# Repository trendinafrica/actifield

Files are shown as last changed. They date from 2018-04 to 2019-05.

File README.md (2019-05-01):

# README  

## Welcome! Or as we say it in Ghana, *Akwaaba!*

This is the Actifield project repository and we’re excited to have you here. 

This document (the README file) is a hub to help you find your way around. Feel free to jump straight to one of the sections below or just scroll down to find our more.

## What are we doing? (and why?)

### The problem

Prohibitive costs is one of the key factors that limit access to science equipment particularly in lesser funded institutions and countries.
This affects the quality of science education and research in these institutions.
As a graduate student I grew frustrated with this problem when I had to modify or abandon some experiments because I did not have the needed equipment.  So I decided to build my own equipment.
I and my friends started this project because we realised we could build some of the equipment we needed on our own by taking advantage of open source designs and code. 
 
### The solution

The [Open Science hardware](http://openhardware.science/) movement has gained popularity in recent years. Using open source designs, code and tools, scientists can now build and customise their own equipment, usually at a fraction of the cost of commercial versions. However, this movement is relatively new to African scientists who may not have the skills to build their own equipment. 

Therefore this project was initiated to build and document some equipment as a step in tackling this problem. We chose to build an actimeter as our first equipment because it is routinely used in experiments in our faculty and the current approach is a very laborious task of manually tracking experiment videos.

## Who we are??
This project was initiated by me, [Victor](https://twitter.com/v_kumbol), and my friends, [Eli](https://twitter.com/AmpofoElikplim) and [Mary](https://twitter.com/mary_twumasi) while we were graduate students at the [Kwame Nkrumah University of Technology](https://www.knust.edu.gh/) in Ghana. 

The project was supported by the generous mentorship and funding we received during the [1st TReND Advanced Open Labware Workshop](http://trendinafrica.org) in April 2018. 

I also received further support and mentorship to reorganise this repository while participating in the 14th Cohort of the Mozilla Open Leaders program.

## What is an actimeter? 
We’re building an equipment called an actimeter. At the simplest, the actimeter is used to measure and record the locomotor activity - how fast or slow a test animal (usually rodents), is moving. This information is useful for several tests such as screening for potentially toxic effects of a new drug on the brain. 

However, beyond these basic tests. An actimeter can be modified to provide more information for example, detecting behaviours in rodents that indicate anxiety or fear. We developed this project for scientists who need a simple and inexpensive actimeter that can be easily built. 

By providing scientists with the resources (designs and code) to build their own actimeter, this project will help scientists in several ways: 
1. Reduce spending for the purchase, repair and maintenance of proprietary equipment
2. Save time by automating laborious tasks e.g. manual video tracking methods
3. Improve teaching since the equipment can be used for practical demonstrations in undergraduate labs 
4. Allow scientists to customise the device for other experiments
5. Increase reproducibility of experiments since the equipment is fully documented

## What do we need
Everyone! In whatever way you can help.

We need expertise in the following areas 
*Neuroscience
*User interface (UI)/ User experience (UX) design
*Computer Aided Design (CAD)
*Electronics
*Arduino
*Technical writing
*Web Development
*Mentorship

## Get involved
If you can help in any of the areas listed above or in any of the many areas that we haven't yet thought of, then please check out our [roadmap](ROADMAP.md) and [contribution guidelines](CONTRIBUTING.md).

Please note that it's very important to us that we maintain a positive and supportive environment for everyone who wants to participate. When you join us we ask that you follow our [code of conduct](CODE_OF_CONDUCT.md) in all interactions both on and offline.

## How can you use it?
If you want to customise Actifield, feel free to download or fork the repository and adapt the content (designs and code) to suit your needs. Everything here is freely reusable.

If you need help with building your own actimeter don’t hesitate to get in touch.

## Contact Us
If you have any questions or suggestions, you can simply open an issue here in this repository. You can also send Victor an <A HREF="mailto:kumbolvictor@gmail.com">email</A>. Wanna hang out on social media? Follow me on [Twitter](https://twitter.com/v_kumbol).

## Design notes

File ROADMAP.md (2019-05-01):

# Roadmap

Hello there!😃 You’re welcome to the Roadmap of the Actifield project. 

This document identifies the project's vision, its current status, and how to reach the project’s end goal. It helps contributors keep track of the overall status of the project and recognize where their help is most needed. Please note that the roadmap is subject to change, and that contributions are also welcome to the document.

## Project Vision
We are working with scientists and developers in Ghana to build a local open hardware community to empower scientists to develop their own lab equipment. We are currently working on upgrading, Actifield, a device for behavioural experiments that we developed for neuroscientists.

## Project Summary
We’re building an equipment called an actimeter. At the simplest, the actimeter is used to measure and record the locomotor activity - how fast or slow a test animal (usually rodents), is moving. More details about Actifield [here](Project_Description.md). 

We developed this project for scientists who need a simple and inexpensive equipment that can be easily built. 
 
## Milestones

Down below are a list of milestones that represent the overall goals of the project. Preferably, they are to be done in sequential order. But you can help in any task you feel comfortable with. Please read our [Contribution Guidelines](CONTRIBUTING.md) and our [Code of Conduct](CODE_OF_CONDUCT.md) 😉

### Short term: During Sprint for Internet Health (May 2019)

- [ ] **Get first community contribution**
> A community member files an issue or adds a pull request.

- [ ] **Display live graphs of activity counts on screen**
> Figure out how to display the results as a live graph on the computer screen. Check out this [issue](https://github.com/trendinafrica/actifield/issues/2)

- [ ] **Display an onscreen grid showing the current location of the mouse in the activity cage**
> Figure out how to determine and show the realtime location of the mouse in the test arena. Check out this [issue](https://github.com/trendinafrica/actifield/issues/3)

- [ ] **Build graphical interface to control the device from the computer**
> More on this [here](https://github.com/trendinafrica/actifield/issues/5)

- [ ] **Check available disk space on SD card before recording counts**
> More on this [here](https://github.com/trendinafrica/actifield/issues/4).

### Medium term: June - August, 2019 

- [ ] **Create manual for users to build or customise the device**
> Write a manual to guide new users to build or customise the device. Check out this [issue](https://github.com/trendinafrica/actifield/issues/6)

- [ ] **Build project website**
> Build website (a [GitHub page](https://pages.github.com/)) to make it easier for users to find and explore our material. with useful resources for African scientists interested in developing their own equipment

- [ ] **Organise training workshop**
> Organise training workshop on building open labware for Ghanaian scientists 

### Completed
- [x] **Build first prototype of Actifield**
> The first prototype of Actified has been built and the designs uploaded onto GitHub.

- [x] **Publish Actifield in a journal**
> Actifield was published in [HardwareX](https://www.sciencedirect.com/science/article/pii/S2468067218300695). This will help provide credibility for academic users and a reference to be cited when used in research works.

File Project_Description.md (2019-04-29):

# Project Description

## Introduction 
The activity meter box is used in neurobehavioral tests to examine the effects of various treatments on the activity level of mice and rats. Our proposed project dubbed “ActiField” is an Arduino-powered activity meter box which can be used to measure locomotor activity of rodents. Locomotor activity is used to evaluate the central effects of drugs. Locomotor activity testing can also reveal possible confounding effects in other tests that rely on motion such as the passive avoidance test for memory. As an additional feature, the ActiField system can be used to automate the open field test, another widely used test for anxiolytic or anxiogenic behaviour. 

## Components
Below is a description of the main components of the ActiField system.

Testing Chamber: The testing chamber is a cuboid plastic box (22×22×30 cm) with a removable transparent cover.

IR Grid: Four panels of 11 IR break beam sensors spaced 2 cm apart are fixed to the inner walls of the testing chamber close to the floor. Each break beam sensor is supplied as a pair of diodes; one diode emits IR beam while the other detects the IR beam. Two panels hold the emitting IR diodes and the other two hold the receiving IR diodes. Receiving and emitting sets will be fixed on opposite sides of the testing chamber to generate a grid of IR beams of 2×2 cm mesh size. As the rodent moves in the testing chamber, the IR beams will be broken and this activity will be transmitted to the microcontroller for processing.

Processing Unit: An Arduino Mega 2560 microcontroller serves as the processor of the system. Inputs from the infrared sensors are fed to the Arduino and processed. The output is displayed online on an attached LCD Screen. Also, a data logging shield is mounted the Arduino for storage of experimental data on an SD. The Arduino can be powered from the mains with a 9 V DC adaptor, a 9 V battery or by a computer.

Display Unit: This consists of a 16×2 LCD screen connected to the Arduino by an i2C LCD backpack. The LCD shows the activity count (total number of beam breaks) and the location of the rodent (centre/periphery) from the system in real time.

## Operation
In our proposed project, ActiField, an Arduino Mega 2560 microcontroller serves as the core processor of the system. Once the code is uploaded to the microcontroller, ActiField can run independently with power from a 9V alkaline battery without the need for a computer or monitor. This is a particularly advantage in settings with erratic or unstable power supply. The system functions automatically and independently according to the code uploaded to the microcontroller. 

Once the system is powered and the code is uploaded, the ActiField system is ready for testing. The mouse or rat to be tested is placed into the test chamber and as the rodent moves in the test chamber it breaks the IR beams in the “grid”. The break beam sensors detect and transmit these signals via the connecting cables to the Arduino. The Arduino keeps a tally of the number of beam breaks and displays the current total on the LCD screen which is mounted on a display unit separate from the test chamber. In most studies, activity counts are expressed at fixed time intervals over the entire test duration. This feature is built into the ActiField system. At a user set frequency (default every 5 min), the Arduino writes the activity count to a file on an SD card mounted on the data logging shield. The user can retrieve this data after the experiment for subsequent analysis on a computer. 
This is the basic functionality of the system however we envisage at least two additional features described below.
Firstly, the ActiField system can be set up to determine the location of the rodent in the test chamber. The IR beams in the test chamber are set up in a grid which represents a coordinate system. Hence, the location of the rodent in the test chamber can be determined based on the set of beams which are broken at a given time. This will require further refinement of the code.
Secondly, the ActiField system can be set up for real time display and graphing of activity counts. This can be made possible by connecting the Arduino to a computer using a USB cable for online display and graphing of the data. We have plans to develop the software to enable this feature using the Processing programming language after building the project. 

## Validation
We intend to validate the system by live video analysis of mice in the test chamber with a video analysis software e.g. Any MAZE or EthoVision concurrently with the ActiField system and comparing the results obtained for correlation.

## Conclusion
In this work, we describe the components and operation of the ActiField system, our proposed real time, automated activity meter box. In this system, low cost components e.g. microcontroller, IR sensors, LCD screen are used to achieve the objectives of the proposed design.

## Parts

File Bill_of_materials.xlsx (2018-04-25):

Part Name | Detail1 | Detail2 | Detail3 | Quantity | Cost per unit | Total cost | Link to supplier/part
Arduino Mega 2560 |  |  |  | 1 | £ 21.99 | £ 21.99 | https://www.conrad.de/de/joy-it-kompatibles-board-arduino-mega-2560r3-1409778.html
Breadboard |  |  |  | 1 | £3.75 | £3.75 | https://www.pollin.de/p/labor-steckboard-510174
Breadboard (empty PCB for soldering) |  |  |  | 20 | £4.09 |  | https://www.conrad.de/de/platine-hartpapier-l-x-b-160-mm-x-100-mm-35-m-rastermass-254-mm-wr-rademacher-wr-typ-790-5-inhalt-1-st-529618.html?sc.ref=Search%20Re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
 |  |  |  | 10 |  | £0.00 | https://www.pollin.de/p/9v-blockbatterien-duracell-industrial-10-stueck-271253
Battery Contact | 9 V |  |  | 10 | £ 0.49 | £ 4.90 | https://www.conrad.de/de/batterieclip-1x-9-v-block-druckknopfanschluss-l-x-b-31-mm-x-14-mm-tru-components-bs-er-36-150-1663957.html
Wire to Board Standard Terminal Block | 12 Contacts |  |  | 3 | £5.48 | £16.44 | http://uk.farnell.com/camdenboss/ctb0708-12/tb-wire-to-brd-12pos-12awg/dp/2315272
Lithium Battery CR1220 | 3 V | 38 mAh | 12.5 mm | 1 | £ 1.19 | £ - | http://uk.farnell.com/multicomp/cr1220/coin-cell-lithium-3v-38mah-cr1220/dp/2065165
soldering iron |  |  |  | 9 | £5.25 | £47.25 | https://www.pollin.de/p/loetkolben-daytools-lk-45w-840195
Solder Wire | 0.7mm |  |  | 1 | £0.82 | £0.82 | http://uk.farnell.com/multicore-solder/d9922-2metre/solder-wire-99-3-0-7-227deg-0/dp/9887105
soldering grease |  |  |  | 9 | £1.15 | £10.35 | https://www.pollin.de/p/loetfett-30-g-840206
Screw driver set | 8 pieces with electic tester |  |  | £1.00 | £7.95 | 71.55 | https://www.pollin.de/p/vde-schraubendreher-set-8-teilig-501143
screw driver set small bits | 36 pieces |  |  | £1.00 | 4.95 | £39.60 | https://www.pollin.de/p/feinmechanik-bitsatz-mit-schraubendrehergriff-36-teilig-501018
Power Distribution Bus |  | 7 x 6mm |  | 8 | $1.95 | $15.60 | https://www.adafruit.com/product/737
IR Break Beam Sensor | 3mm LED |  |  | 25 | $1.95 | $48.75 | https://www.adafruit.com/product/2167
Jumper wires |  | 65 units bundle |  | 4 | $3.50 | $14.00 | https://www.pollin.de/p/steckbruecken-sortiment-65-teilig-511007
crocodile cable (get a LOT) |  |  |  | 12 | $2.95 | $35.40 | https://www.pollin.de/p/messleitungen-mit-krokodilklemmen-0-5-mm2-200-mm-10-stueck-830593
Adafruit Assembled Data Logging shield for Arduino |  |  |  | 1 | $13.95 | $13.95 | https://www.adafruit.com/product/1141
i2c / SPI character LCD backpack |  |  |  | 1 | $9.95 | $9.95 | https://www.adafruit.com/product/292
Standard LCD 16x2 + extras | White on Blue |  |  | 1 | $9.95 | $9.95 | https://www.adafruit.com/product/181
multimeter |  |  |  | 5 | 19.95 | $99.75 | https://www.pollin.de/p/multimeter-mastech-ms8233e-ce15-830722
MikroSD karte | 16gb | class10 |  | 5 | 5.99 | 29.95
wire stripper |  |  |  | 9 | 3.25 | 29.25 | https://www.pollin.de/p/automatik-abisolierzange-500070
Packing tape | 6 units set |  |  | 2 | 4.99 | 9.98 | https://www.pollin.de/p/klebeband-kinzo-6er-set-891200
Electrical tape |  |  |  | 9 | 2.95 | 26.55 | https://www.pollin.de/p/elektriker-isolierband-19-mm-18-m-weiss-temperaturbestaendig-511240
LEDs |  |  |  | 2 | 1.95 | 3.9 | https://www.pollin.de/p/leuchtdioden-sortiment-100-teilig-800002
resistors | high power |  |  | 1 | 3.95 | 3.95 | https://www.pollin.de/p/sortiment-hochlast-widerstaende-1-17-w-100-stueck-800027
ribbon cable | 16wires | 28awg |  | 10 | 2.57 | 25.7 | https://www.conrad.de/de/flachbandkabel-rastermass-127-mm-16-x-008-mm-bunt-3m-7000058337-meterware-604069.html
allen key set | 10 pieces |  |  | 16 | 1.95 | 31.2 | https://www.pollin.de/p/innensechskant-schluesselsatz-10-teilig-501921
wire stripper |  |  |  | 9 | 3.25 | 29.25 | https://www.pollin.de/p/automatik-abisolierzange-500070
IR emitter | 5mm led |  |  | 25 | $0.81 | $20.25 | https://www.conrad.de/de/ir-emitter-940-nm-40-5-mm-rund-radial-bedrahtet-lite-on-lte-5208a-1127316.html
IR Detector | 5mm led | 940nm |  | 25 | $0.76 | $19.00 | https://www.conrad.de/de/ir-detektor-rund-radial-bedrahtet-5-mm-940-nm-20-lite-on-ltr-3208e-1127310.html

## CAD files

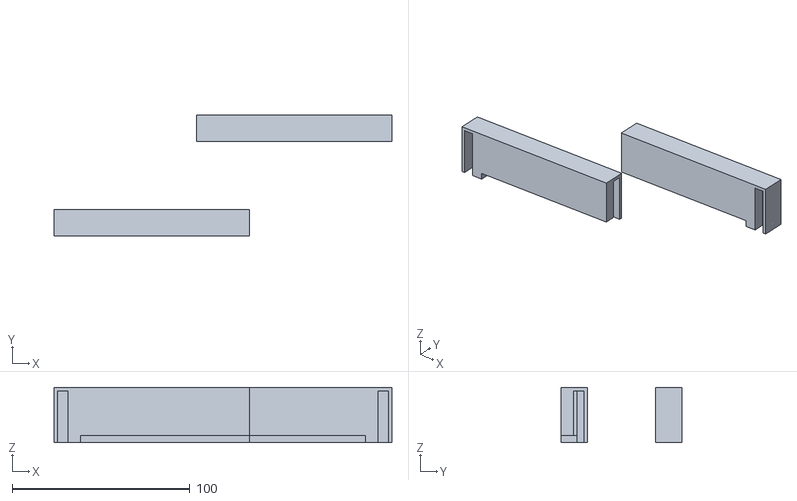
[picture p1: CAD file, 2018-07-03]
3D_print_designs/IR Panel B top.stl
190.0 x 68.0 x 31.0

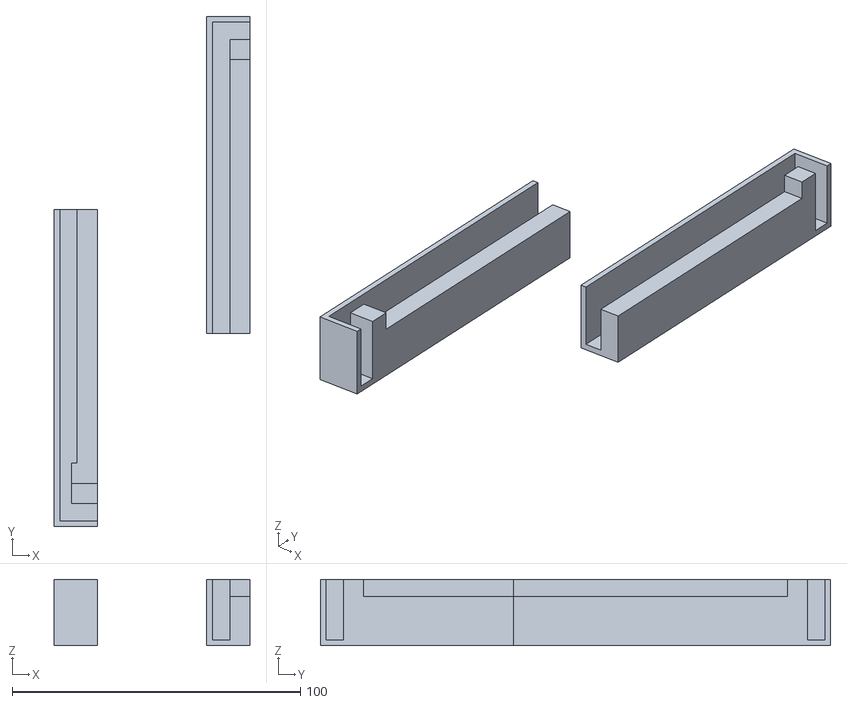
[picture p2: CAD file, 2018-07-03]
3D_print_designs/IR Panel B bottom.stl
68.0 x 177.0 x 23.0

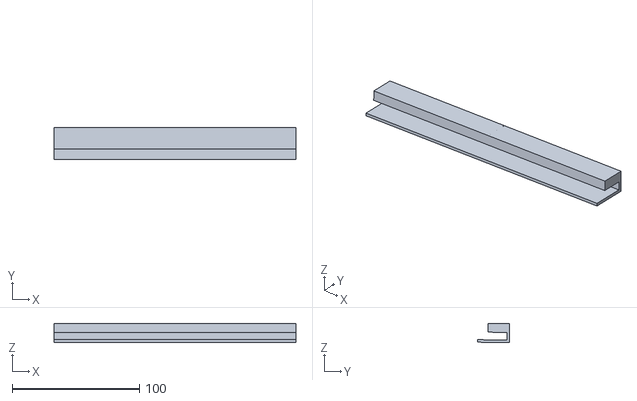
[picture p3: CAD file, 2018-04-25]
3D_print_designs/IR Panel A bottom.stl
190.0 x 25.3 x 15.3

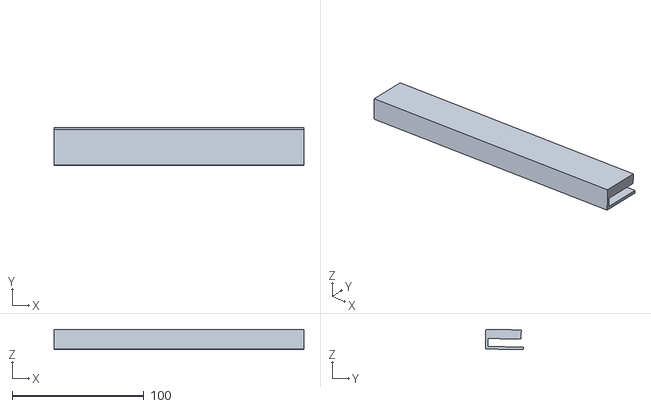
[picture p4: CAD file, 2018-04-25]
3D_print_designs/IR Panel A top.stl
190.0 x 29.0 x 15.5

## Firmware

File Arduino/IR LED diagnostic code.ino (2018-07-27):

int outPin = 13; // the pin number of the indicator LED
int outPinState = LOW; // the current state of the indicator LED
int count = 0; //this variable will store the number of beam breaks
int limit=50;                 //Threshold for detecting IR radiation 

// the following variables are long because the time, measured in miliseconds,
// will quickly become a bigger number than can be stored in an int.
long outTime = 0; // the last time the output pin was toggled

 //rows and cols will define the size of the array 
const int rows = 2;
const int cols = 8;
String pin;

int SensorMatrix[rows][cols] = {
  // This matrix will hold the pin assignments for the Sensors
  {0, 1, 2, 3, 4, 5, 6, 7}, 
  {8, 9, 10, 11, 12, 13, 14, 15}
};

int SensorStateMatrix[rows][cols] = {
 // This matrix will store the current reading from each sensor
  {0, 0, 0, 0, 0, 0, 0, 0},
  {0, 0, 0, 0, 0, 0, 0, 0}
};


void setup() {
Serial.begin(9600); //initialize serial monitor for writing
pinMode(outPin, OUTPUT); //set outPin as an output pin
} //close setup()

 
void loop() {
 
  //this nested for loop will scan each IR sensor in sequence
  for(int i = 0; i < rows; i++){
 
    for(int j = 0; j < cols; j++){
  SensorStateMatrix[i][j] = analogRead(SensorMatrix[i][j]); //read the current value of the corresponding sensor
  // if the beam was just broken (i.e. the sensor value went from > limit to <= limit) or restored (i.e. the sensor value went from <=limit to > limit),
    //int pin_no = SensorMatrix[i][j]+ 1
    pin = String(SensorMatrix[i][j] + 1);
    Serial.print("Pin "); 
    Serial.println(pin);  
    Serial.print(" reading = "); 
    Serial.println(SensorStateMatrix[i][j]);  
    delay(5); 
  }
 
    }//close for j
     Serial.println("");  
     Serial.println("");  
     Serial.println("");  
     delay(5000);
  }//close for i
 

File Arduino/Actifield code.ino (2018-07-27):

/*Created 7 July 2018
By Victor Kumbol
*/


#include <Wire.h>
#include <LiquidCrystal_I2C.h> //import libraries for LCD screen
#include <SD.h> //import the SD Card library
#include <SPI.h>

LiquidCrystal_I2C lcd(0x27,16,2);


int count = 0; //this variable will store the number of beam breaks
int threshold = 400; //Threshold for detecting IR radiation.This sets the sensitivity of the sensors
long runTime = 0; // this variable records the duration of the current test
long syncTime = 0; //this variable stores the last time the data was stored ot the SD card

File logfile; // the logging file


const long SYNC_INTERVAL = 60000; //mills between calls to flush()
const int chipSelect = 4; //the output pin for the SD card

String Sensor; //this stores the string type of the current sensor
String Count; //this variable stores the string type of the current beam-break count

int minutes;
int seconds;
int errors = false;

 //rows and cols will define the size of the array that stores pin assignments for the IR sensors
const int rows = 2;
const int cols = 8;


int SensorMatrix[rows][cols] = {
  // This matrix will hold the pin assignments for the IR sensors
  {0, 1, 2, 3, 4, 5, 6, 7},
  {8, 9, 10, 11, 12, 13, 14, 15}
};

int SensorStateMatrix[rows][cols] = {
 // This matrix will store the current reading from each sensor
  {0, 0, 0, 0, 0, 0, 0, 0},
  {0, 0, 0, 0, 0, 0, 0, 0}
};

int lastSensorStateMatrix[rows][cols] = {
 // This matrix will store the previous reading from each sensor
  {0, 0, 0, 0, 0, 0, 0, 0},
  {0, 0, 0, 0, 0, 0, 0, 0}
};


void setup() {
Serial.begin(9600); //initialize serial monitor for writing
pinMode(4, OUTPUT); // set the default chip select pin to output
initialize();
}


void loop() {
scan_sensors(); //call function to scan the IR sensors
display(); //call function to display results on LCD screen
log_data(minutes, count);  //call funtion to store results to SD card
}

//This function will initialize the IR sensors, lcd display and data logger to ensure they are working properly
void initialize() {
//initialize lcd screen for display
  lcd.init();
  lcd.backlight();
  lcd.clear();
  lcd.print("Booting system");
  delay(5000);

//Test all the sensors and report an error if any of them isn't working.
  lcd.clear();
  lcd.print("Testing sensors");
  delay(5000);

  for(int i = 0; i < rows; i++){
      for(int j = 0; j < cols; j++){
      SensorStateMatrix[i][j] = analogRead(SensorMatrix[i][j]); //read the current value of the corresponding sensor
      if (SensorStateMatrix[i][j] < threshold){
        // if the reading from a sensor < threshold, toggle errors as true.
        errors = true;
        delay(20);
        }
      }
    }

    if (errors) {
      error("IR sensors faulty"); //report errors with sensors if any
    }
    else {
      lcd.clear();
      lcd.print("IR sensors OK");
      delay(2000);
    }

      // initialize the SD card
      Serial.print("Testing SD card.....");
      lcd.clear();
      lcd.print("Testing SD card");
      delay(5000);
      // see if the card is present and can be initialized:
      if (!SD.begin(chipSelect)) {
        error("SD card failed"); //report error with SD card if detected
      }
      Serial.println("SD card OK");
      lcd.clear();
      lcd.print("SD card OK");
      delay(2000);

      // create a new file
      char filename[] = "LOGGER00.CSV";
      for (uint8_t i = 0; i < 100; i++) {
        filename[6] = i/10 + '0';
        filename[7] = i%10 + '0';
        if (! SD.exists(filename)) {
          // only open a new file if it doesn't exist
          logfile = SD.open(filename, FILE_WRITE);
          logfile.println("time (min),activity count");
          break;  // leave the loop!
        }
      }

      if (! logfile) {
        error("file not created"); //report error with creating a file, if any
      }

      Serial.print("Logging to: ");
      Serial.println(filename);
      lcd.clear();
      lcd.setCursor(0,0);
      lcd.print("Logging to: ");
      lcd.setCursor(0,1);
      lcd.print(filename);
      delay(2000);

      Serial.println("time (min),activity count");

    lcd.clear();
    lcd.print("Setup Complete");
    delay(2000);
    lcd.clear();

}//close initialize


void scan_sensors(){
  //this function will scan all the sensors one after the other to detect beam breaks
  for(int i = 0; i < rows; i++){
    for(int j = 0; j < cols; j++){
  SensorStateMatrix[i][j] = analogRead(SensorMatrix[i][j]); //read the current value of the corresponding sensor
  if (SensorStateMatrix[i][j] <= threshold && lastSensorStateMatrix[i][j] > threshold) {
  // if the beam was just broken (i.e. the sensor value dropped below the threshold) increment count and record the time
    count += 1;
    Sensor = String(SensorMatrix[i][j] + 1);
  }
  lastSensorStateMatrix[i][j] = SensorStateMatrix[i][j];
 delay(2);
    }

  }
     delay(50);
return;
}


void display() {
  //display total count of beam breaks
  runTime = millis();
  minutes = runTime/60000;
  seconds = (runTime%60000)/1000;
  lcd.setCursor(0,0);
  lcd.print("Time:" + String(minutes) + "min " + String(seconds) + "s");
  lcd.setCursor(0,1);
  lcd.print("Count:" + String(count));
  return;
}

void error(char *str){
  Serial.print("Error: ");
  Serial.println(str);
  lcd.clear();
  lcd.setCursor(0,0);
  lcd.print("Error: ");
  lcd.setCursor(0,1);
  lcd.print(str);
  while(1);
}

void log_data (int a, int b){
  //check if the time interval after the last data logging session is equal to the sync interval
  if ((millis() - syncTime) < SYNC_INTERVAL) {
    return;
  }

  if (a < 1){
    a=1;
    }

  // log minutes since starting to the SD card
  logfile.print(String(a));           // milliseconds since start
  logfile.print(", ");
  Serial.print(String(a));         // milliseconds since start
  Serial.print(", ");

//log the activity count to the SD card
  logfile.print(String(b));
  logfile.println();
  Serial.print(String(b));
  Serial.println();
  logfile.flush();
  syncTime = millis();
}

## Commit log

2018-04-18 Four Sensors
    This code allows the Arduino to monitor beam breaks from four IR sensors.
2018-04-20 16 LED Analog
    This code works for 16 LED sensors. It basically scans each sensor in sequence and reports when a beam is broken or restored as a count.
2018-04-25 Laser cutting designs
    These are the designs for the sides of the Actifiled chamber to be cut using a laser cutting machine.
2018-04-25 Code updated for 16 IR sensors
2018-04-25 Designs for 3D printed parts
    [Emitter_panel_bottom-1.stl, Emitter_panel_bottom-2.stl, Emitter_panel_top-1.stl, Emitter_panel_top-2.stl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]
2018-04-25 Updates on designs
    1. Renamed some folders
    2. Included the bill of materials
    [Bill_of_materials.xlsx, Emitter_panel_bottom-1.stl, Emitter_panel_bottom-2.stl, Emitter_panel_top-1.stl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]
2018-04-27 Updates in code
    I implemented a more object oriented design by using functions. I also included an initialisation stage to test the sensors. Finally, I included outputs to the lcd screen
2018-07-03 Rename sides_1.svg to Test Chamber side_A.svg
2018-07-03 Rename chamber_floor.svg to Test Chamber floor.svg
2018-07-03 Rename sides_2.svg to Test Chamber side_B.svg
    Rename sides_2.svg to Test Chamber side_B.svg
2018-07-03 Rename top.svg to Test Chamber cover.svg
    Rename top.svg to Test Chamber cover.svg
2018-07-03 Renamed several files
    [IR Panel A bottom.stl, IR Panle A top.stl]
2018-07-03 Renamed files
    [Emitter_panel_bottom-1.stl, Emitter_panel_bottom-2.stl, Emitter_panel_top-1.stl, Emitter_panel_top-2.stl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]
2018-07-03 Schematics of circuitry included
    [Schematics.fzz]
2018-07-27 updated arduino code
